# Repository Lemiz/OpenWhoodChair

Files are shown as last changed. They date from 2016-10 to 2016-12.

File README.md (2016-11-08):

# OpenWoodChair

This is a fork of the [OpenWheelChair](http://www.openwheelchair.org/). We dropped the PVC pipes and use palette wood instead so that the wheelchair gets cheaper to build, targeting a wider audience especially in developing countries.

We implemented the BYU wheelchair during the 2016 Abylimpics event in Bordeaux, France, and turned the pipes to wood during the Fabrikarium hackathon organized by MHKit in collaboration with the Airbus group in Octobre 2016 at the Airbus facility in Toulouse, France. Working language: French. 

You may also refer to the French version of Open wheelchair on MHKit website: http://myhumankit.org/tutoriels/fauteuil-roulant/

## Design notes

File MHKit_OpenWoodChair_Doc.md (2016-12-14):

# Présentation du projet

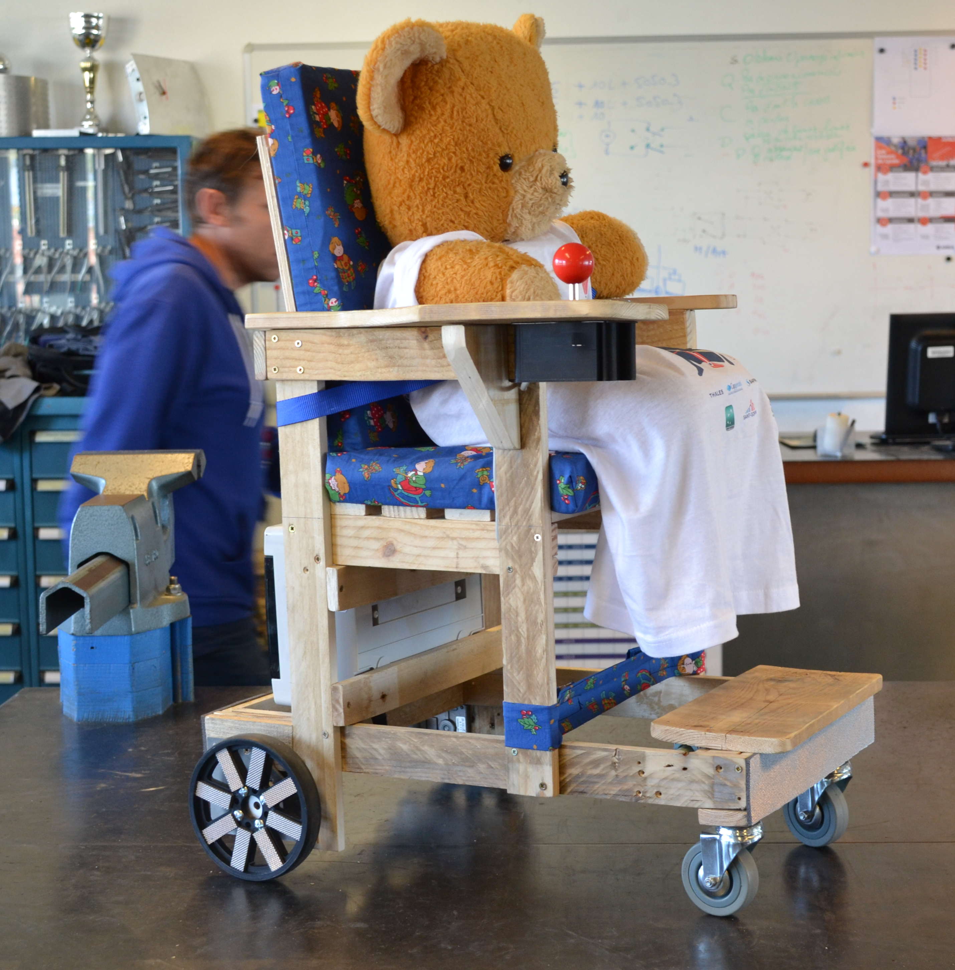
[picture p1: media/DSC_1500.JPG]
Alt Vue du fauteuil assemblé en fin de sprint Fabrikarium Airbus
 *Vue du fauteuil assemblé en fin de sprint Fabrikarium Airbus*
 
OpenWoodChair est une adaptation par l'association My Human Kit du projet Open wheel chair par la fondation américaine du même nom. Le but, que nous partageons avec cet organisme de bienfaisance, est de proposer une liste de pièces, des plans et un manuel de montage pas à pas permettant l'autoconstruction d'un fauteuil roulant en bois motorisé et à faible coût destiné aux enfants. L'idée est de rendre cet équipement réalisable avec un minimum de moyens techniques, en proposant de recycler un maximum de pièces, dont la maintenance et l'évolutivité soient également garanties. Il s'agit d'un processus en constante évolution, qui est documenté ici et publié sous des licences CC-BY permettant son libre usage tout comme sa modification et sa redistribution.

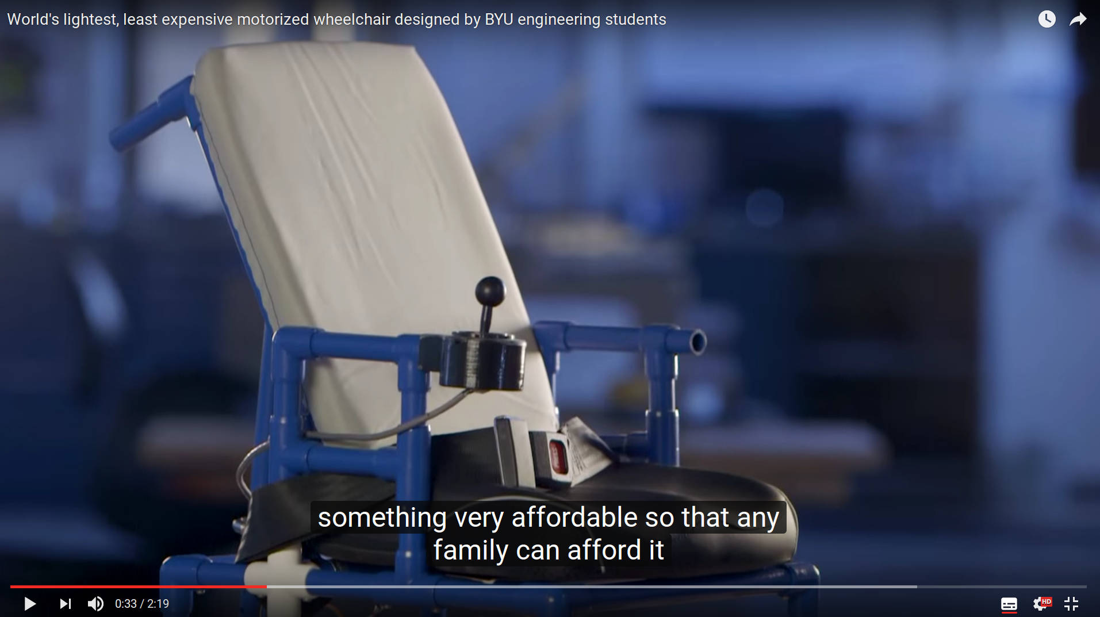
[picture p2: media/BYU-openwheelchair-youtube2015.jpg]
Alt Image extraite de la vidéo de présentation du projet Openwheelchair
. 
*crédits: Brigham Young University News*

La principale innovation du projet OpenWhoodChair réside dans l'abandon des tubes PVC disponible uniquement sur le marché nord-américain de l'ossature au profit d'un matériau recyclé disponible à peu près partout sur la planète, à savoir du bois de palette. On peut également imaginer d'autres adaptations à partir de ressources locales disponibles en abondance à proximité de chez vous, comme le bambou pour l'ossature, du tissu produit localement pour les coussins, etc.
Dans l'idée de rendre le fauteuil compatible avec une propulsion manuelle, nous avons également déplacé les roues motrices de l'avant à l'arrière, de telle sorte qu'il est toujours possible d'assembler le fauteuil sans les moteurs électriques avec de grandes roues classiques.
# Licences
Le matériel est distribuée sous licence CERN Open License Hardware v1.2.  
Sauf mention contraire, toutes photos et illustrations CC 3.0 BY-SA Olivier Heinry.

# Crédits & remerciements

Le projet initial est accessible sur le site de la [fondation Open Wheel Chair](http://www.openwheelchair.org/).

## Sprint Abilympics, Bordeaux, Avril 2016 
Bernadette et Gérard Véron, Jimmy Véron, Yvonne et René Véron, Madeleine et Jean-Louis Delahaye, Jacqueline et Michel You
## Sprint Fabrikarium , Lycée Airbus, Toulouse, Octobre 2016 
Michel & Jacqueline You , Gérard & Bernadette Véron ( afficionados MHK), Patrice Navarri (Airbus Toulouse), Jean-François Soucaille (Airbus Toulouse), Dirk Thalheim (Airbus HH) pour les conseils et retours utilisateur, Marine du Lycée Airbus (pilote d'essai), Olivier Heinry (FLOSS Manuals) pour la documentation, Philippe Pacotte (sympathisant MHK) pour la modélisation et l'impression 3d. 
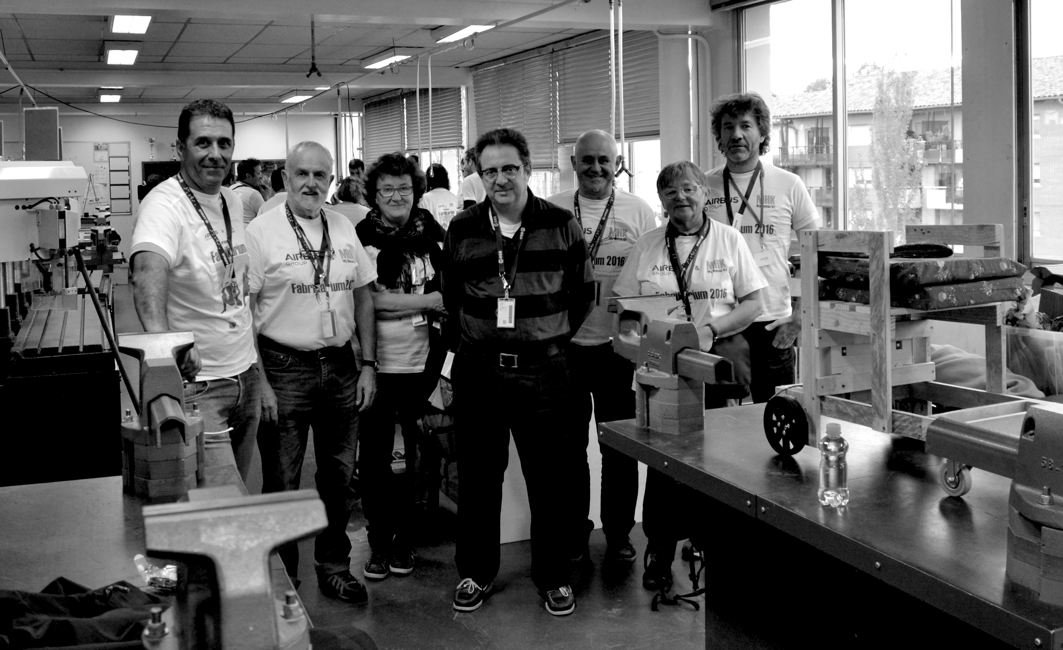
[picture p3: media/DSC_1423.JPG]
Photo de groupe FabrikariumAirbus. Absents: Dirk, Marine & Philippe
 *Photo de groupe lors du Fabrikarium Airbus. Absents: Dirk, Marine & Philippe*

# Avertissement

La liste des pièces et certaines sections de la documentation ne sont pas définitives. Elles seront plus proches de la réalité lors de la prochaine itération au collège Petite Lande de Rezé (44) lors de la semaine du Handicap en 2017. Si d'ici là vous vous lancez dans l'assemblage d'un fauteuil et trouvez des corrections ou voulez soumettre des améliorations, n'hésitez pas à forker le [dépôt Github](https://github.com/MHKit/OpenWhoodChair) et soumettre des pull requests.

# Liste des pièces & fournitures
## Ossature bois
Toutes les pièces de bois de palette suivantes ont une section approximative de 50 x 14 mm.

+ accoudoirs
    
    + montants arrière : 2 x 450mm
    + montants avant : 2 x 530mm2 x 350mm
    + repose-pieds et siège : 7 x 350mm
    
+cadre inférieur

   + 2 x 600mm
   + 4 x 313mm
   + 2 x 83mm
   + 2 x 36mm

+ supports moteur
   + 2 x 83mm
   + 2 x 110mm
+ traverses latérales du siège : 4 x 300mm
+ traverses arrières du siège :
   + 1 x 278mm
   + 1 x 310mm
   + 1 x 345mm
+ repose-pieds: 1 planche de 340 x 140

Métrage total utilisé : 10m. Prévoir de débiter 12m.

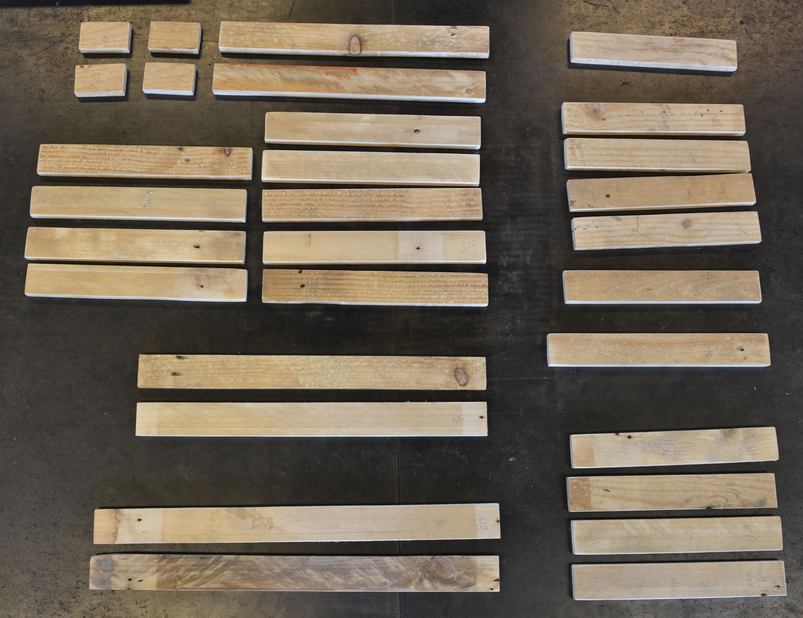
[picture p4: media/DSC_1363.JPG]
Alt Planches débitées. Manquent 2 pièces longueur 110 et 2 pièces de 36mm
 *Planches débitées. Manquent 2 pièces longueur 110 et 2 pièces de 36mm*
+ dossier du siège
   + contreplaqué 9mm : 270x400mm. 

### Astuce
+ Si vous souhaitez rendre les pièces de bois plus durable,vous pouvez les passer à l'huile dure ou bien à l 'huile de lin diluée avec 5-10 % de térébenthine.
+ Pour le contreplaqué, utilisez du bois d'intérieur classé E1, dont les colles dégagent peu de COV toxiques. 

/* màj flossmanuals s'arrête ici */

## Groupe de propulsion
* Plaques de fixation des motoréducteurs  
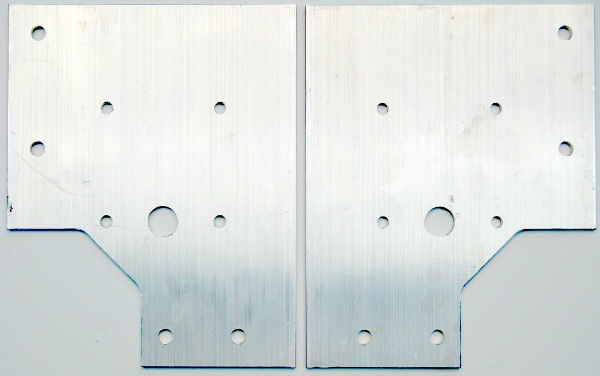
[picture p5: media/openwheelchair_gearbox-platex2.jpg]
plaque de support du motoréducteur
 *plaque de support du motoréducteur*

Ces plaques sont utilisées pour monter les motoréducteurs sur le châssis. Référence GEARBOX-PLATE 14,95$ le lot de 2 chez [www.openwheelchair.org] (http://www.openwheelchair.org/Products/GearBox-Plate/) US$ 14,95 + frais de port
Vous pouvez également les usiner vous-même. Les plans sont en ligne sur https://github.com/OpenWheelchair/Wheelchair-Frame malheureusement dans un format fermé (Solidworks).
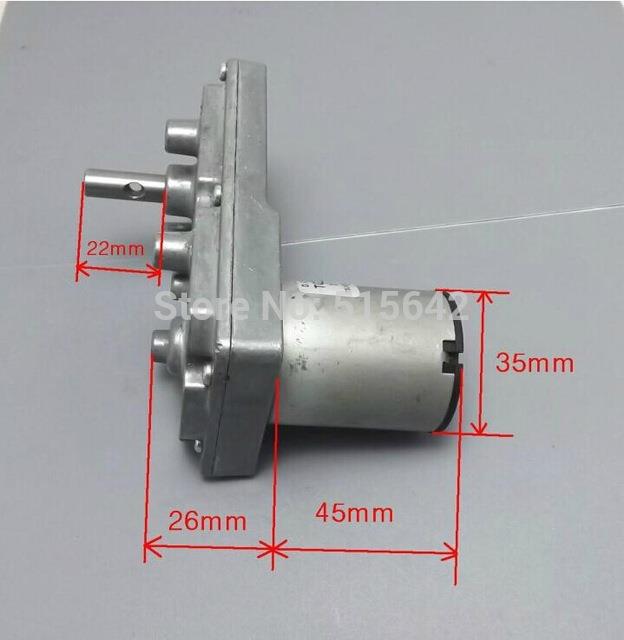
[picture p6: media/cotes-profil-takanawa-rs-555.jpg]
Alt motoréducteurs
* 2 motoréducteurs Takanawa RS-555  *Motoréducteur*

Budget : 10 à 20 US$ sur Ebay ou Aliexpress. 

+ 2 roues folles diamètres 100mm
+ 2 roues pleines diamètre 6 pouces (soit 18 cm) avec un axe diamètre M4 (référence Openwheelchair)

## Coussins & ceinture
### Assise
* mousse d'épaisseur 50mm: 350 x 270 
* tissu : deux pièces de 350 x 390 mm
* 2 bandes velcro aka scratch  à coudre de 5 x 2,5cm

### Dossier
* mousse d'épaisseur 50mm: 390 x 300 
* tissu : deux pièces de 350 x 470 mm
* 2 bandes velcro aka scratch  à coudre de 5 x 2,5cm

### Cale-pieds
* 1 lanière de tissu de 120 x 900mm

### Ceinture de sécurité
* 1 sangle avec une boucle de serrage

### Marquage
Découpe de bandelettes réfléchissante dans des plaques d'isolant métallisé réfléchissant pour porte de garage avec une face adhésive. 

+ Bande arrière 370 x 50 mm
+ Bandelettes de dimensions variables à disposer sur les roues motrices

## Visserie & quincaillerie
### Visserie bois
+ vis de 3 x 25 mm (3,5 x 25mm également possible)
+ x vis de 4 x 35 mm
+ x vis de 4 x 45 mm

#### Astuces
+ Il vaut mieux éviter les vis à tête fendue ou Philips qui sont fragiles ne permettent pas d'exercer beaucoup de force lors du vissage et privilégier les têtes Pozidriv ou Torx.
+ Afin d'accélérer le montage, faites en sorte d'utiliser un seul type et une seule taille d'embout. Par exemple, nous n'avons utilisé que du PZ2 lors du montage de notre prototype.

### Visserie métallique
+ 8 boulons poêliers 5 x 50mm

### Quincaillerie
+ Axe du repose-pieds  
   + un bout de tringle à rideau ou un tuyau de plomberie de 340mm de longueur
   + 2 colliers simples de plomberie dont le diamètre est le double de la tringle ou du tuyau
+ 2 écrous et 2 rondelles du diamètre des roues folles 
+ Un bib de colle à bois vinylique prise rapide

## Electronique & électricité
+ un joystick à contacts fin de course
+ 1 Arduino/Genuino Uno
+ un PCB DFrobot DC Motor Driver 2×15A - Lite ref. SKU:DRI0018
+ un interrupteur
+ du câble électrique souple 0,75mm2
+ 1.5m de câble Ethernet 4 paires
+ une batterie 12V
+ un connecteur à barillet (dit jack)
+ un boitier électrique étanche. Le modèle utilisé ici: Coffret étanche DEBFLEX 12 modules - ref : 706722 : H : 20 cm, L : 27 cm, P : 12 cm. Il doit surtout être assez grand pour loger batterie, circuit de charge, Arduino et driver
+ une vingtaine de câbles Dupont mâle/mâle 20cm  de couleur

## Outillage
Vous aurez besoin des outils suivants pour assembler le fauteuil roulant, disponibles dans n'importe quel magasin d'outillage. Le seul outil spécialisé dont vous aurez besoin (il s'agit de l'extracteur de pignon) est optionnel, et n'est nécessaire que si vous souhaitez passer à des moteurs plus puissants.
### Electroportatif
* une perceuse à colonne OU une perceuse filaire SINON une visseuse sans fil fera l'affaire
* une visseuse sans fil OU un jeu de tournevis
* une ponceuse OU du papier de verre grain 50, grain 120 voire plus fin si vous tenez à avoir une finition d'ébéniste
* une meuleuse avec disque métal peut être utile pour couper les boulons et vis à bois trop longs
* une machine à coudre OU une aiguille et de l'huile de coude

### Outillage manuel
* Jeu de clés 6 pans dites Allen (métrique)
* Jeu d'embouts type Pozi driv ou Torx suivant votre approvisionnement en vis
* Forets à bois diamètre 2,75 (ou 3) et 6
* un fer à souder 30W et un peu de brasure
* un mètre ruban métallique
* une équerre
* un niveau à bulle
* un crayon à bois et/ou une pointe sèche
* des colliers de serrage électrique parfois appelés Rilsan ou Colson
* des cosses électriques plates
* un multimètre
* des serre-joint OU presse à bois OU des pinces-étau
* du frein-filet faible résistance type Loctite 222 OU du vernis à ongle
* un pied de biche, une masse & des tenailles pour le recyclage des palettes
* un masque à poussière, des bouchons d'oreilles, des lunettes de protection, des gants de manutention
* des ciseaux de couturière et un mètre ruban souple
* une règle 50+ cm qui ne marque pas le tissu

### Option: extracteur de pignon 
Utilisé pour retirer le pignon du moteur d'origine pour le remplacer par un moteur plus puissant. Quelques références en ligne:

+ AliExpress  : Puller-Remover-Walkera-W010
+ Hobbyking.com : Product id : S630

# Instructions de débit du bois de palette

## Étape 1: Mesures de votre enfant
Les cotes données dans la liste des pièces correspondent à la stature d'un enfant de 4 ans (taille de 102 cm. Source: http://www.labonnetaille.com/guide-des-tailles/enfant-bebe-mode-vetements). Si votre enfant est particulièrement grand, vous pouvez rallonger de quelques dizaines de millimètres les cotes des accoudoirs et des montants arrière et avant, éventuellement la profondeur du siège. Par contre, le châssis sur lequel sont fixés roues et moteurs ne doit pas voir ses dimensions évoluer.

## Étape 2 - Acheter et rassembler les matériaux et  outils 
Procurez-vous les différents matériaux figurant sur les pages "liste des pièces" et "liste d'outils". Si vous ne trouvez pas certaines pièces, libre à vous d'adapter aux matériaux disponibles à proximité.

## Étape 3 – Démonter les palettes
Il existe beaucoup de qualités différentes de palettes, qui peuvent servir à transporter de tout, entre autres des produits toxiques. Faites donc bien attention dans le choix de votre matière première.  Privlégiez les palettes portant le marquage NIMP 15 ressemblant à un épi de blé et les initiales HT, signifiant qu'elles ont subi un traitement thermique non-toxique contrairement au marquage BM signifiant un traitement au bromure, nocif. Ce dernier est interdit au sein de l'UE depuis 2010.

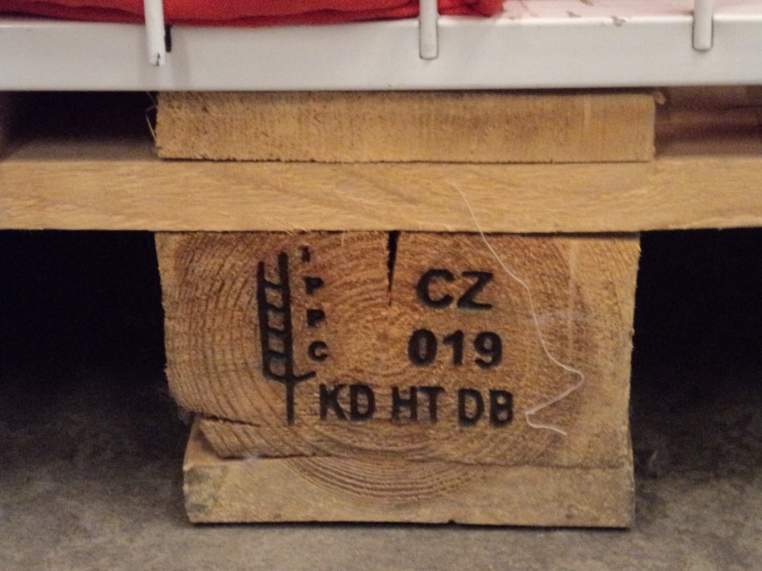
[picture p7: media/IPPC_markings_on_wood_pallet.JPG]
Alt By self-made by the uploader - Own work, CC BY-SA 2.5 ca, https://commons.wikimedia.org/w/index.php?curid=25071284
 
*self-made by the uploader, CC BY-SA 2.5*

Choisissez des palettes fraîchement assemblées, le bois séché exerçant plus de contrainte lors du retrait des clous et agrafes.

#### Astuce
N’oubliez pas de porter vos équipements de protection lors du démontage: lunettes de protection, gants et bouchons d'oreille, chaussures de sécurité et  vaccin contre le tétanos.

Posez la palette à l'envers sur votre plan de travail. Avec le pied de biche, ôtez les clous des semelles: commencez par la planche du milieu, elle est  plus facile à enlever. Réservez les planches.

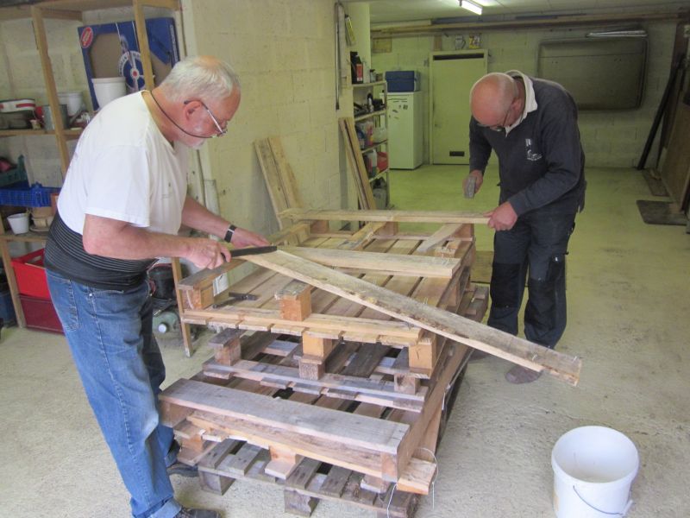
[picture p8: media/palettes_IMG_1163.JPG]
 
*CC 3.0 BY-SA Jacqueline You*

Posez ensuite la palette au sol toujours sur le dos (son plancher) et chassez les chevrons (les blocs quadrangulaires) avec la masse.

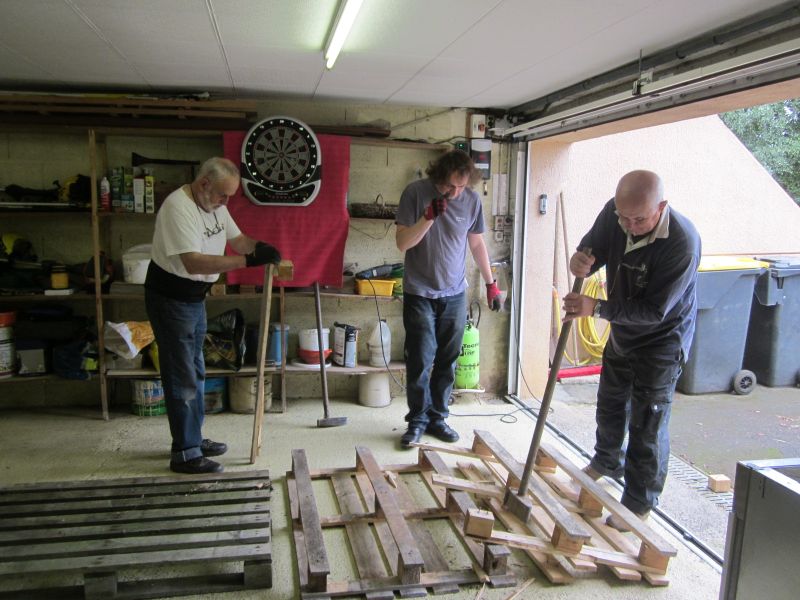
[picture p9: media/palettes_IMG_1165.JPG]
 *CC 3.0 BY-SA Jacqueline You*

Une fois ceci fait, il faut retirer les agrafes et clous restants. On commence par marteler les agrafes du côté des chevrons et on finit de les extraire avec les tenailles.

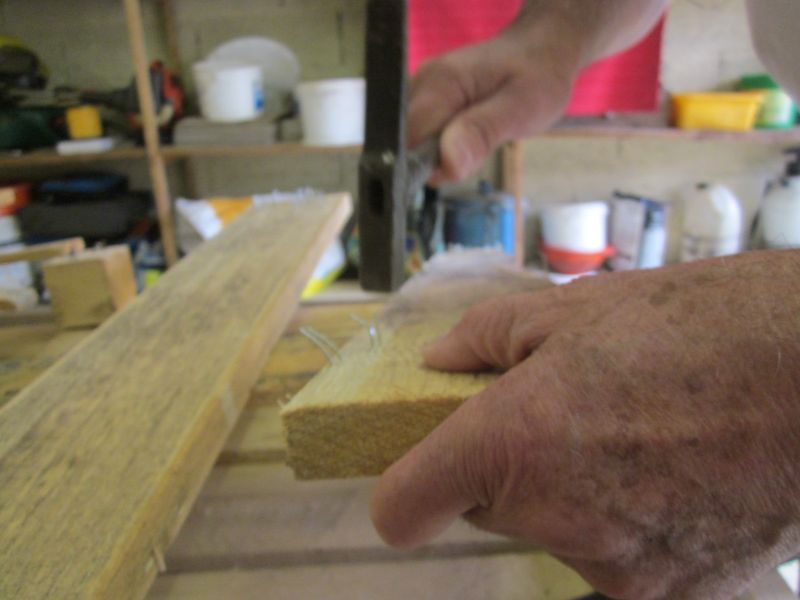
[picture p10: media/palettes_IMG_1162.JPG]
 
*CC 3.0 BY-SA Jacqueline You*

On récolte ça:

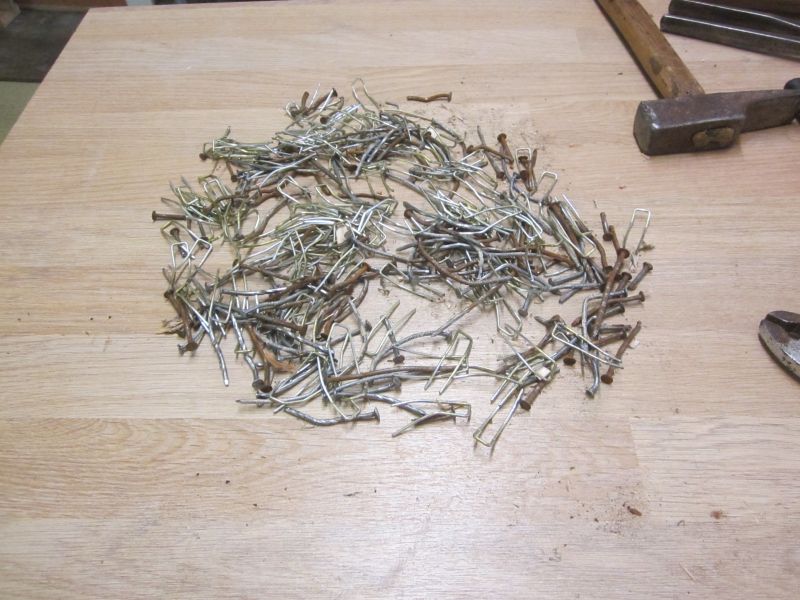
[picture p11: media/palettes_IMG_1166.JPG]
 
*CC 3.0 BY-SA Jacqueline You*

Finalement,on passe au ponçage des planches afin de faire disparaître les échardes , étape au cours de laquelle le port du masque est hautement recommandé. Vous voilà avec un stock de matière première!

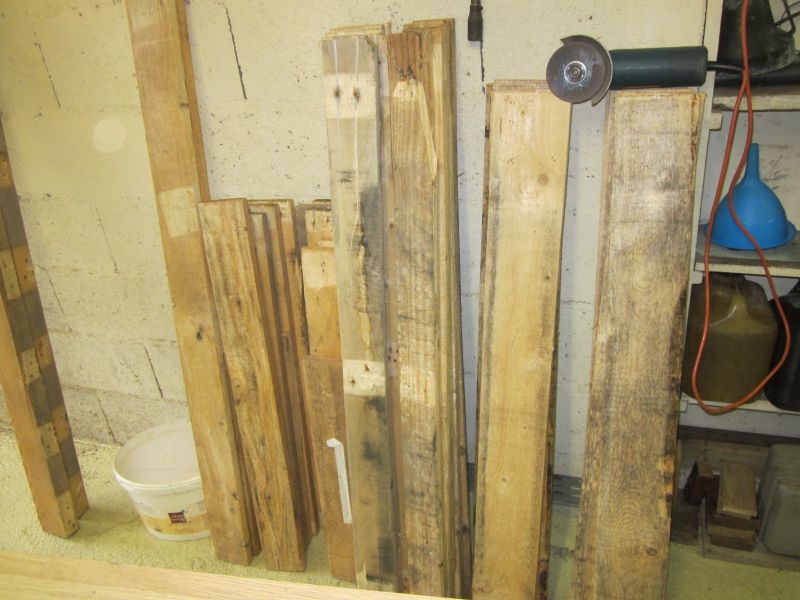
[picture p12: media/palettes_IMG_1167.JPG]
 
*CC 3.0 BY-SA Jacqueline You*

## Etape 4 - Débiter le bois de palettes
On commence par débiter les planches les plus longues, en faisant attention aux nœuds, potentiellement cassants, où aux fentes qui sont apparues au démontage, particulièrement de bois sec. Vous pouvez le faire avec une scie électrique à onglet, à défaut avec une scie à main dans une boîte à onglet. Reportez-vous au paragraphe Ossature bois du chapitre précédent pour consulter la liste des planches nécessaires.

version électroportative *version électroportative*
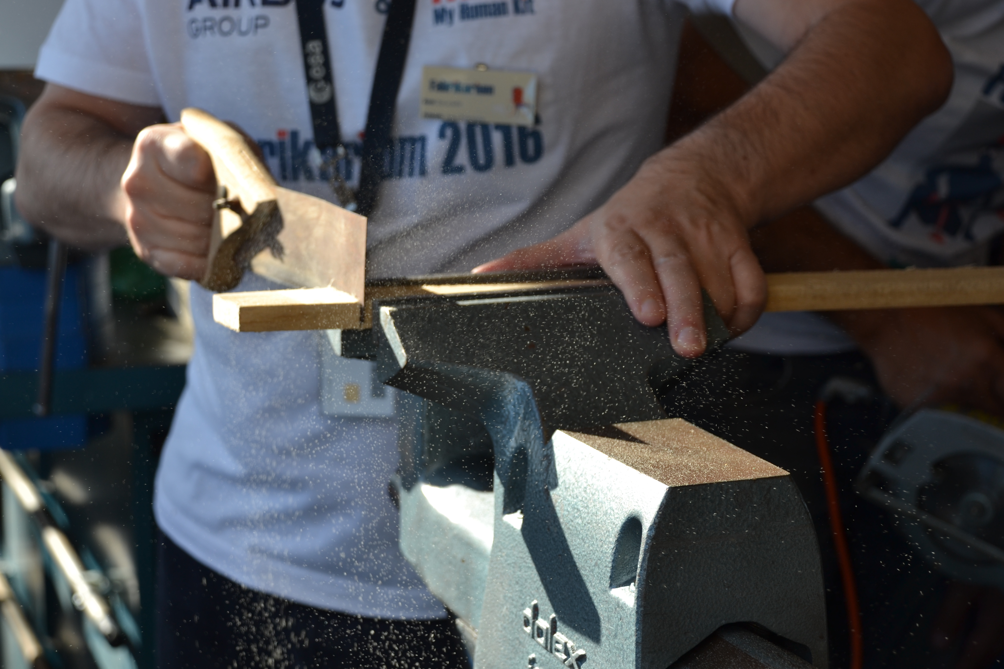
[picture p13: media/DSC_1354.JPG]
Alt version manuelle
 *version manuelle*
Il est également utile de casser les angles vifs après le débit en passant rapidement la ponceuse inclinée à 45°.

# Instructions de montage
Le cadre en bois sera assemblé en 2 parties: tout d'abord la base,  puis les accoudoirs et enfin le siège avec son dossier. Le bloc propulsion, le repose-pieds et les coussins seront assemblés à la toute fin.

## Préparation de gabarits

Afin de garantir la régularité de l'alignement des perçages, nous commençons par construire deux gabarits de perçage. Le premier servira à réaliser les préperçages de bout de planche et le second pour les  préperçages latéraux. 

#### Gabarit de vissage de bout
Prenez une chute, découpez son extrémité proprement à 90°. Tracez ensuite un trait parallèle à l'extrémité à une distance correspondant à la moitié de l'épaisseur du bois de palette. Exemple: si votre bois de palette fait 14mm d'épaisseur, vous tracez un trait à 7mm de l'extrémité pour que la vis pénètre au coeur du bois. Vous percerez ensuite 2 trous à 10 mm de chaque bord avec un foret à bois d'un diamètre en dessous du diamètre de vos vis, afin que le fil puisse encore mordre le bois sans pour autant le faire éclater.

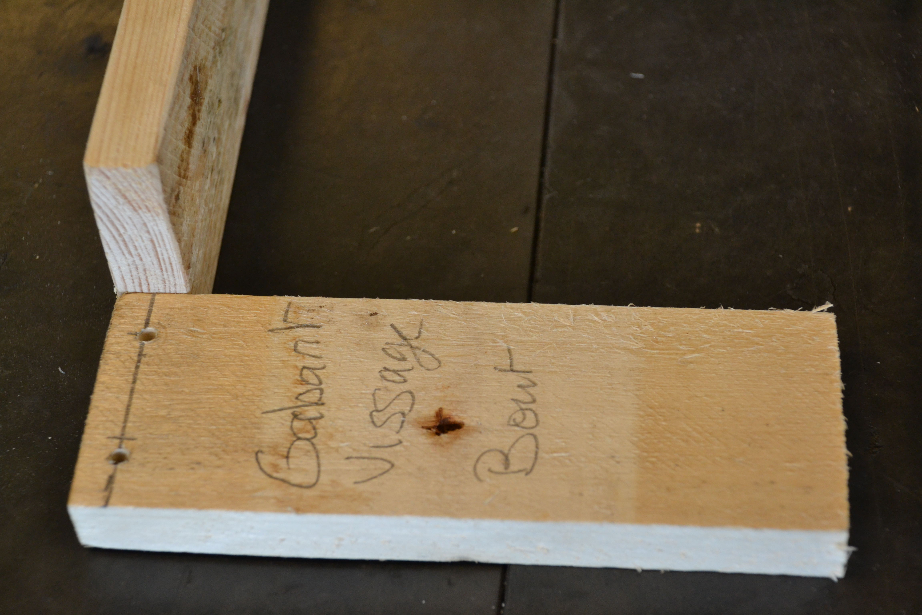
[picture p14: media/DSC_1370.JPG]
Alt gabarit de bout
 

*gabarit de bout*

#### Gabarit de vissage latéral
Prenez une chute, découpez son extrémité proprement à 90°. Tracez ensuite un trait parallèle à l'extrémité à une distance correspondant à la largeur du bois de palette (dans notre cas, 50mm). Tracez ensuite les diagonales. Vous percerez ensuite 4 trous à 15 mm de chaque angle avec le même foret que précédemment.
Alt gabarit latéral 

*gabarit latéral*

#### Astuce
L’assemblage va beaucoup plus vite si vous organisez vos planches en paquets suivant les dimensions. Vous pouvez noter la cote directement sur la pièce comme nous l'avons fait ici au porte-mine, note qui sera enlevée par ponçage une fois l'assemblage fait.

## Assemblage de la base du châssis
### Assemblage du cadre
Rassemblez les différentes pièces nécessaires à cette étape:
+ vis 3x25mm
+ vis 4x35mm
+ 2 x 600mm
+ 4 x 313mm
+ 2 x 83mm
+ 2 x 36mm

On commence par prépercer les planches de 600mm en utilisant le gabarit de vissage de bout. On se contente de marquer sans traverser la planche.
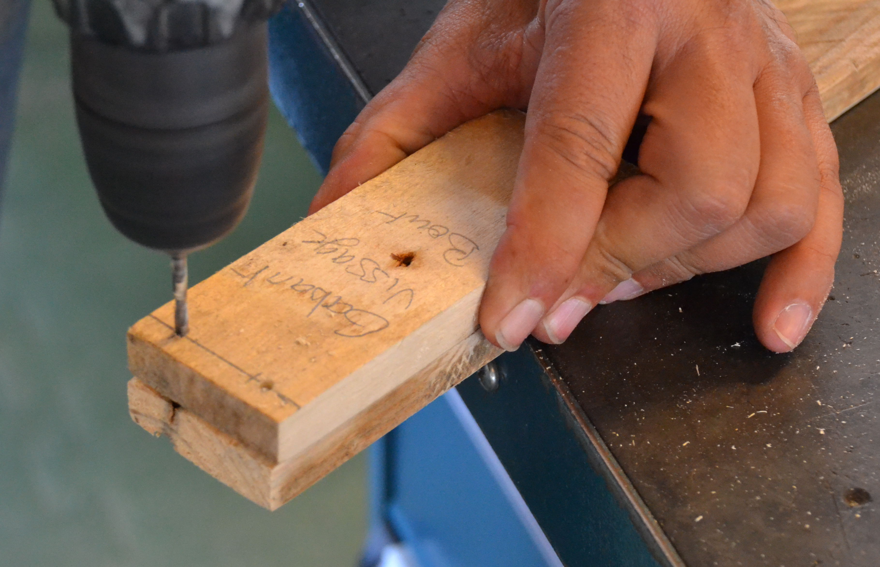
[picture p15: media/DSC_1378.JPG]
Alt préperçage à l'aide du gabarit
 *préperçage à l'aide du gabarit*

On passe ensuite au perçage proprement dit. Cela permet de vérifier que le bois ne fend pas, ou que le perçage n'a pas lieu à un endroit critique comme un noeud ou l'ancien emplacement d'un clou.
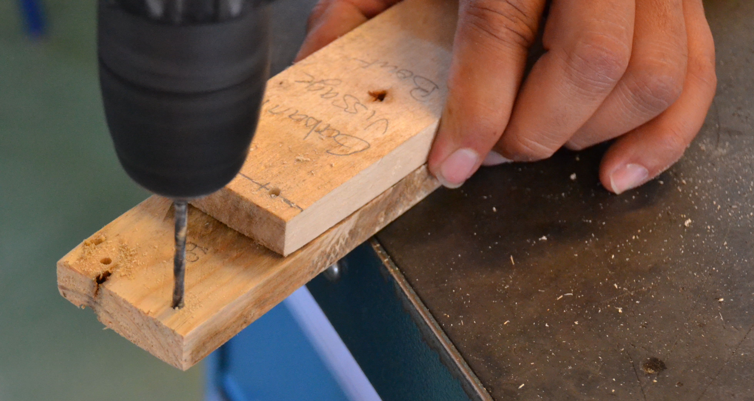
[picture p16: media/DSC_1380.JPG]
Alt Perçage proprement dit
 *Perçage proprement dit*

Disposez ensuite les  2 planches de 313 mm à l'intérieur des planches de 600mm, en vérifiant le bon équerrage. On visse en 4x35mm. Vosu devez obtenir un cadre rectangulaire, pas un trapèze. 
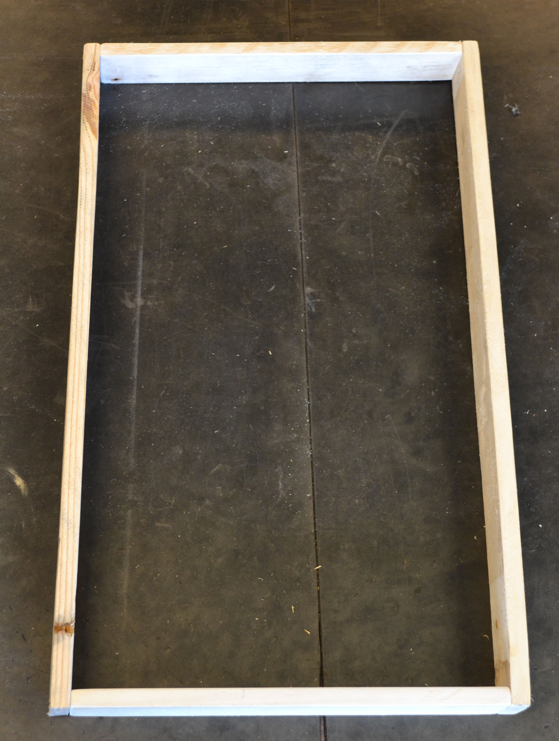
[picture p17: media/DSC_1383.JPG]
Alt Cadre assemblé
 *Cadre assemblé*

### Ajout de renforts
Nous devons maintenant assembler 2 planches de 83mm à l'intérieur des planches de 600mm, au niveau de ce qui portera les futures roues motrices. On commence par marquer l'épaisseur de la planche, puis on utilise la gabarit de vissage latéral aligné sur cette marquer pour prépercer la première vis.
Alt Préperçage du renfort *Préperçage du renfort*

On visse avec deux vis 3x25; attention de ne pas noyer la tête pour seulement affleurer du côté intérieur.
Alt Vissage du renfort *Vissage du renfort*

On peut ensuite assembler la traverse de 313mm avec quatre vis 4x35 pour obtenir un montage dont on vérifiera l'équerrage avant de visser définitivement.
Alt Assemblage des renforts et de la traverse *Assemblage des renforts et de la traverse*

On répète l'opération à l'autre extrémité. Attention: il faut utiliser les entretoises de 36mm à l'avant, contrairement à ce qu'indique la photo! En effet, nous avons ajouté par la suite un repose-pieds basculant qui a nécessité de déplacer vers l'avant la traverse. 
Alt Assemblage final du cadre *Assemblage final du cadre*

## Assemblage des accoudoirs

Rassemblez les différentes pièces nécessaires à cette étape:
+ montants arrière : 2 x 450mm
+ montants avant : 2 x 530mm
+ traverses latérales du siège : 4 x 300mm
+ 12 vis 3x25mm
+ de la colle à bois

Disposez face à vous en les alignant les extrémités des 4 montants. Utilisez le gabarit de vissage latéral pour marquer 2 préperçages à chaque extrémité. Marquez ensuite chaque montant d'un trait à 245mm de l'extrémité prépercée. Répétez l'opération de préperçage.
Alt Nous avions ici déjà assemblé la traverse du haut. Il est plus aisé de commencer par le marquage simultané de tous les montants avant assemblage. *Nous avions ici déjà assemblé la traverse du haut. Il est plus aisé de commencer par le marquage simultané de tous les montants avant assemblage*

Assemblez ensuite 2 traverses de 300mm avec un montant de 450mm et un montant de 530mm. 
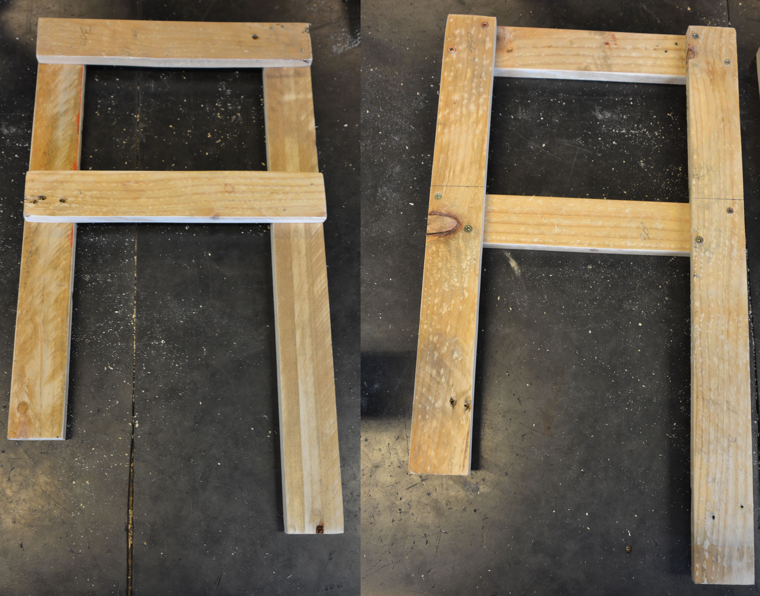
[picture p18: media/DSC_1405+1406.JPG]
Alt Vue recto-verso du premier accoudoir
 *Vue recto-verso du premier accoudoir *

Répétez l'opération pour l'accoudoir suivant, avec les 4 montants du côté opposé. Lors de l'assemblage final, les traverses du bas supporteront l'assise et celles du haut la tablette horizontal de l'accoudoir.

Marquez ensuite le montant de 530mm à 80mm de l'extrémité laissée libre et utilisez le gabarit de vissage latéral pour y faire 2 prépercages. Prépercez également le montant de 450mm.
Alt Le bon usage de l'autofocus facilite la lecture du mètre-ruban :) *Le bon usage de l'autofocus facilite la lecture du mètre-ruban :)*

Vous pouvez alors assembler le premier accoudoir en l'alignant à la verticale du trait à 80mm à la base du chassis et l'extrémité du montant le plus court. L'arrière de montant le plus long doit se caler à l'extrémité de la traverse du chassis.
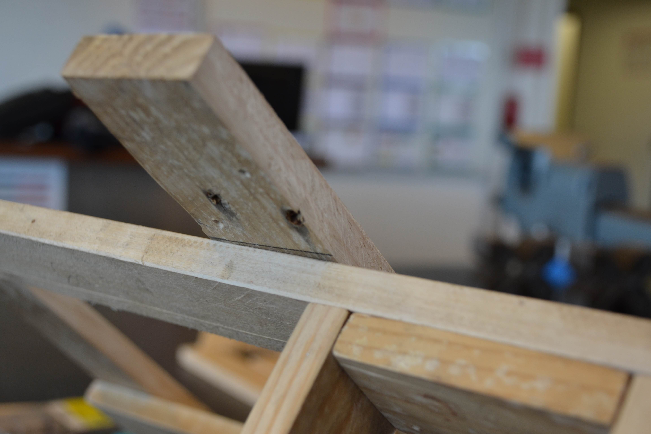
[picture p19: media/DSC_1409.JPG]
Alt Vue d'ensemble
 *Vue d'ensemble*

On doit ajouter de nouveaux renforts qui doivent mieux répartir les fortes contraintes liées à l'assemblage des roues motrices à cet endroit. Ces pièces doivent courir de l'extrémité du cadre jusqu'aux montants arrière des accoudoirs. Il vaut mieux les mesurer plutôt que de les couper au préalable. Dans notre cas, elles font 112mm au lieu des 110mm prévus. Ce n'est pas bien méchant, mais tant qu'on y est...
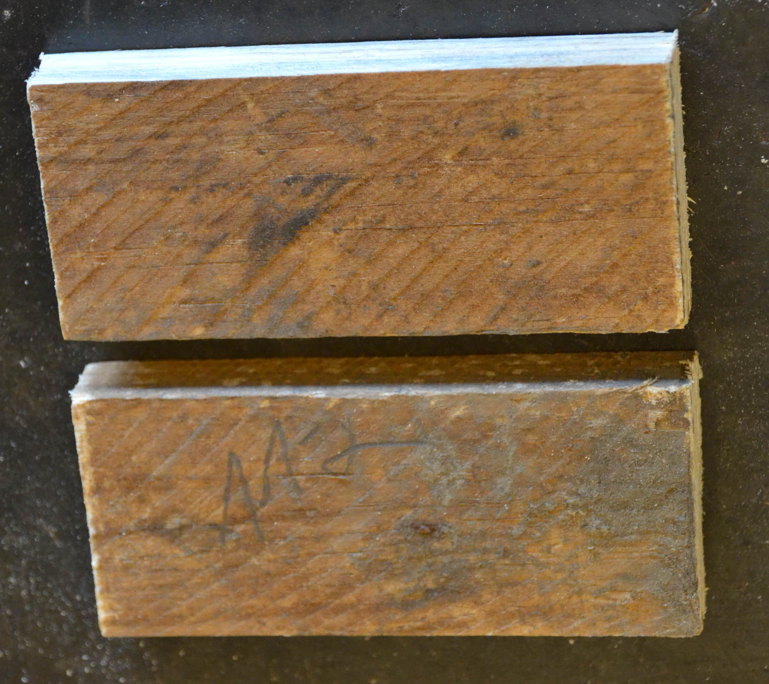
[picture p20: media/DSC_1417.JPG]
alt Cales de 110mm qui font 112mm dans la vraie vie
 *Cales de 110mm qui font 112mm dans la vraie vie*

On est libre d'utiliser le gabarit de vissage latéral ou pas. Un peu de colle à cet endroit ne peut pas faire de mal non plus.
Alt Cales assemblées *Cales assemblées*

## Montage des roulettes
Rassemblez les différentes pièces nécessaires à cette étape:
+ traverse: 1 x 345mm
+ 2 roues folles diam. 100mm
+ 6 vis 4x35mm
+ de la colle à bois

On commence par visser la traverse horizontale de 345mm sur laquelle seront fixées les roues folles en travers de l'avant du chassis. On utilisera le gabarit de vissage de bout, en travers tout d'abord pour les deux premières vis, puis à 90° sur la traverse avant, où une seule vis suffira. 
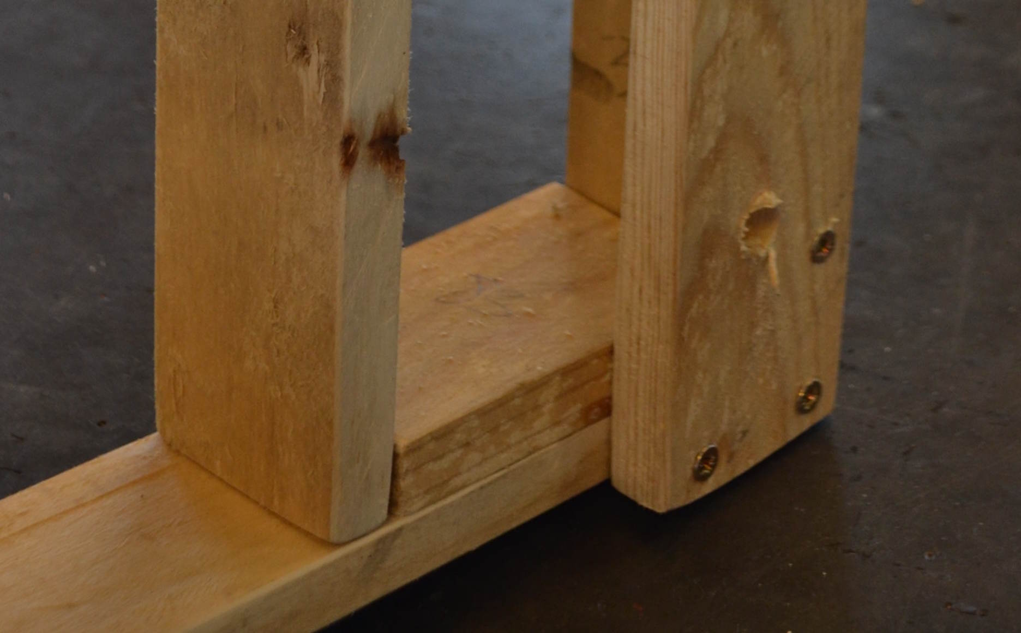
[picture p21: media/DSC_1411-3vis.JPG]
Alt Détail de l'assemblage avec les entretoises de 83mm.
 *Détail de l'assemblage avec les entretoises de 83mm*

On perce ensuite la traverse que nous venons de poser pour laisser passer les axes des roues folles. Le dimaètre de perçage dépend du diamètre de ces axes. Dans notre cas, il s'agissait de M6. On perce alors directement en 8mm sans chercher à utiliser un diamètre inférieur contrairement aux vissages effectuées précedemment, car on boulonne. La position latérale du perçage doit être déterminé en fonction de la largeur totale du fauteuil roulant une fois les roues arrières montées. Il faut ques les roulettes avants puissent pivoter librement à l'intérieur de la largeur totale. Quant à la position en profondeur du perçage, elle a été déterminée de telle sorte que la rondelle et l'écrou puissent être assemblés sur l'axe de la roue folle sans encombre.
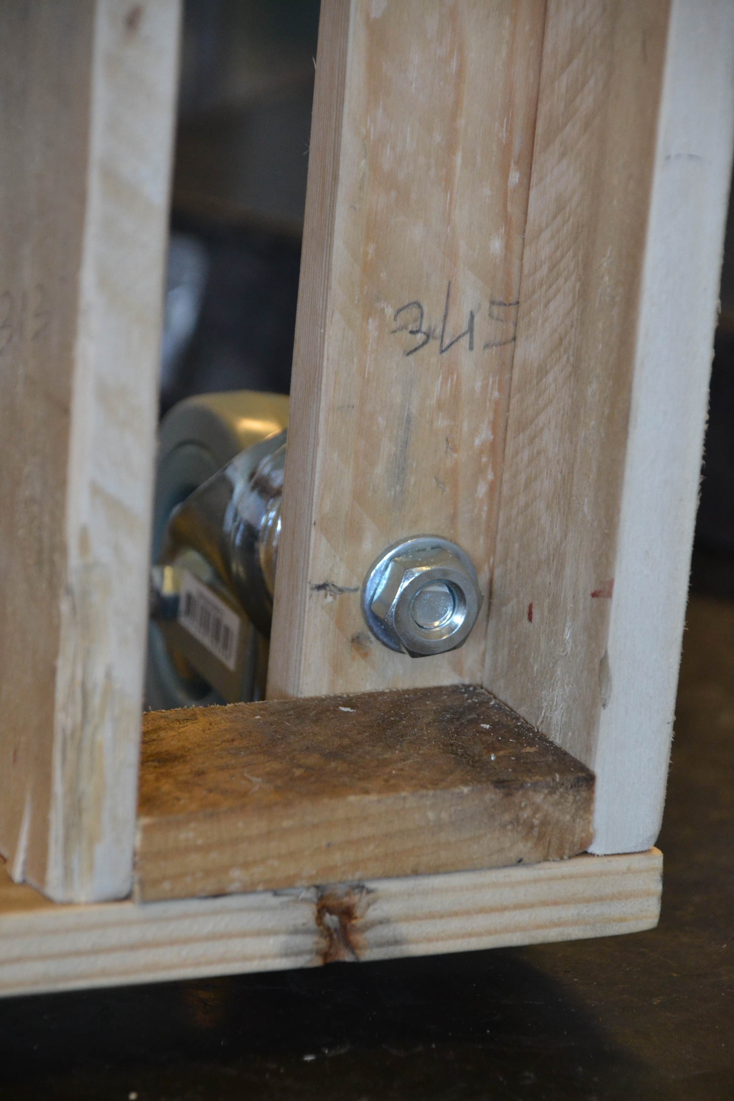
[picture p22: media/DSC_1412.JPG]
Alt Détail du boulonnage avec les entretoises de 83mm.
 *Détail du boulonnage avec les entretoises de 83mm*

Votre assemblage final doit plutôt ressembler à cette illustration. Comme nous devons régler finement plus tard la hauteur, ne serrez pas trop fort.
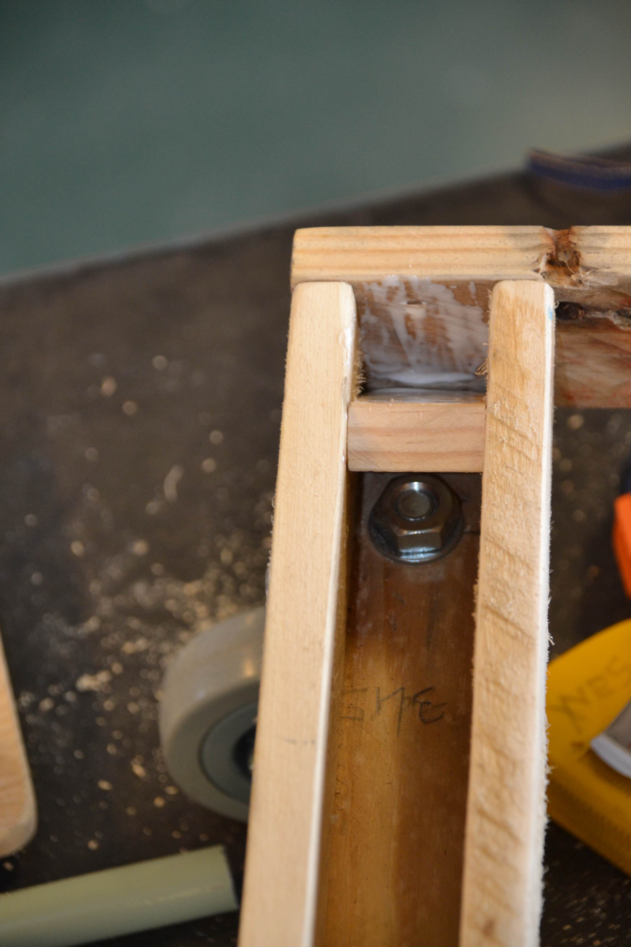
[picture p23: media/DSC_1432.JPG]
Alt Détail du collage a posteriori d'une entretoise de 36mm.
 *Détail du collage a posteriori d'une entretoise de 36mm*

## montage des roues motrices

Rassemblez les différentes pièces nécessaires à cette étape:
+ 2 plaques de fixation des motoréducteurs
+ 2 motoréducteurs Takanawa RS-555
+ 2 roues pleines diamètre 150mm et leurs moyeux
+ 8 boulons poêliers 5 x 50mm + écrous
+ 8 vis m4 x 30mm tête fraisée
+ 4 vis à bois 4 x 45mm
+ 4 vis à bois 2 x 25 mm
+ clé Allen

Nous commençons par assembler la plaque au motoréducteur, puis la roue à l'ensemble. Une fois fait, on soude les câbles d'alimentation électrique. Une fois les 2 roues assemblées, on les fixe au chassis de bois.

### assemblage de la plaque au motoréducteur.
Si vous utilisez des vis à tête fraisé, il vous faudra au préalable fraiser les 8 perçages de petit diamètre, par exemple avec un foret HSS 6mm. Si vous utilisez des vis à tête plates, vous pouvez y aller.
Perçages à utiliser  *Perçages à utiliser cerclés*

Présentez les plaques face au moteur en faisant coïncider les perçages M4 cerclés sur l'illustration . Vissez en utilsant 4 vis m4 après avoir déposé une goutte de freinfilet à mi-filetage. Répétez l'opération avec l'autre ensemble, en faisant attention à l'orientation. Les 2 assemblages sont symétriques et non pas identiques.

### assemblage de la roue 
Assemblez la roue sur son moyeu en répartissant également les quatre boulons poêliers. N'hésitez pas encore une fois à mettre une goutte de freinfilet.
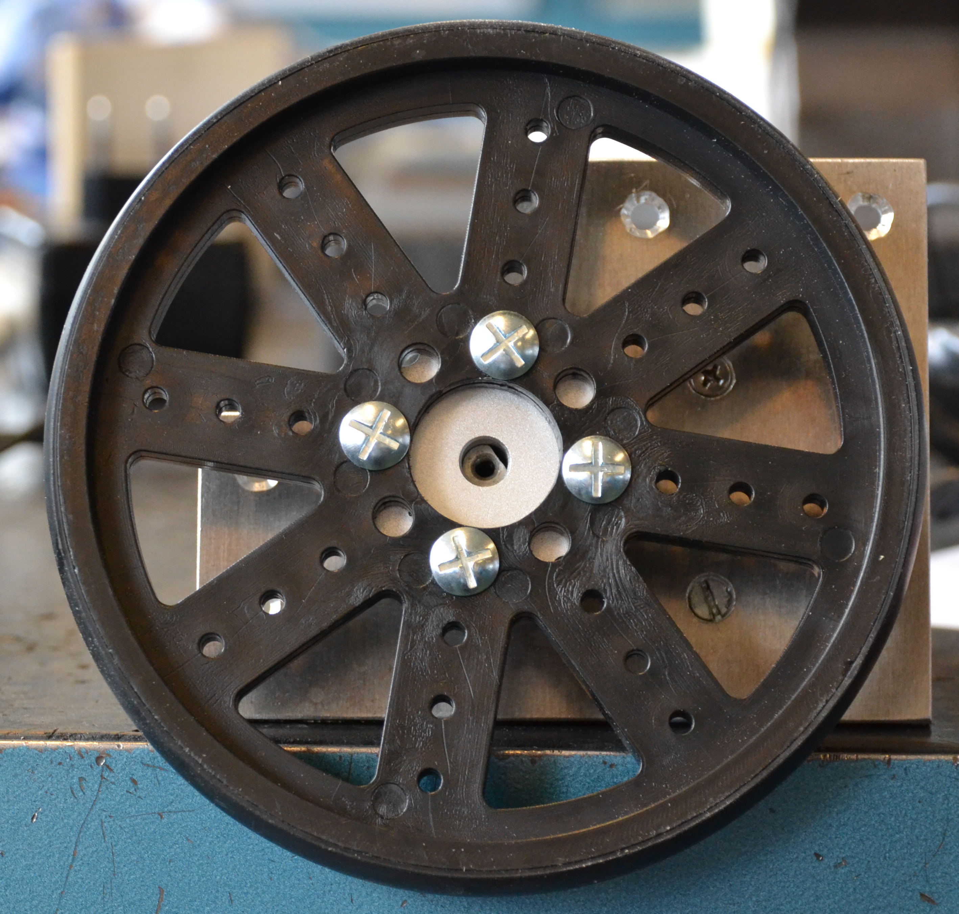
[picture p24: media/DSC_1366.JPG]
Alt Vue latérale de l'assemblage.
 *Evitez d'utiliser des vis cruciformes et fendues comme nous l'avons fait ;-)*
Présentez la roue sur l'axe du moteur. La vis de serrage doit être présentée face au méplat de l'axe. On utilise une clé Allen pour ce faire. Alt vue masse de l'assemblage *Vous pouvez raccourcir les boulons à la meuleuse si vous jugez qu'ils risquent de frotter contre la plaque.*

### montage de l'ensemble
C'est ici une étape cruciale pour le futur comportement roulant du fauteuil. Pour que le fauteuil file droit lorsqu'il court sur son erre, les roues motrices sont disposées à l'arrière. Pour éviter que les roues folles ne se bloquent, leur axe vertical doit être parfaitement vertical. A vous de jouer entre le réglage des boulonnages à l'avant et la hauteur à laquelle vous vissez les blocs moteurs à l'arrière. Pour ce faire, il vaut mieux travailler sur un établi parfaitement horizontal, il suffit de le vérifier à l'aide d'un niveau à bulle. Vous posez ensuite le fauteuil sur cales à l'arrière et sur ses roues folles à l'avant et trouvez la bonne hauteur en vous aidant du niveau à bulle posé parrallèlement à l'axe d'une des roues folles. Vérifiez ceci des deux côtés, sinon le  fauteuil aura tendance à virer.
Ceci fait, vous pouvez présenter votre bloc moteur-roue sur le chassis en présentant la découpe de la plaque par l'avant. Faites un marquage, puis fixez la plaque  en utilisant les vis 4 x 45 mm sur la partie arrière renforcée et les vis 3 x 25mm sur le montant arrière du siège. Vous pouvez passez le tournevis au travers des rayons de la roue.

Alt Vue latérale du montage 
*Vue latérale du montage*

## Fabrication des accoudoirs et boîtier du joystick

Les accoudoirs sont différents mais interchangeables: il suffit de les retourner lorsque vous les changez de côté. L'un des accoudoirs est spécifique en ce qu'il a une forme de palette (de peintre) destinée à abriter le joystick. Vous trouverez le plan au format SVG sur notre dépôt Github dans le dossier  src (https://github.com/oli44/OpenWhoodChair-1/blob/master/media/accoudoir.svg) ainsi que celui de l'équerre de l'accoudoir (https://github.com/oli44/OpenWhoodChair-1/blob/master/media/equerreAccoudoir.svg). Le perçage central mesure 6mm de diamètre, les préperçages de vis à bois sont variables, au minimum le diamètre de votre boulon/vis - 0,5mm de diamètre afin qu'il y ait un peu de friction au serrage.

Alt Plan coté de l'accoudoir 
*Plan coté de l'accoudoir*

Alt Plan coté de l'équerre de l'accoudoir 
*Plan coté de l'équerre de l'accoudoir*

## câblage et impression 3d du boitier du joystick
Afin d'abriter les contacts électriques du joystick de l'arrachement accidentel ou des projections d'eau, il est recommandé de l'abriter dans un boitier isolant. Nous avons modélisé et imprimé un boitier en ABS sur mesure. Vous trouverez les fichiers source sur notre [dépôt Github](https://github.com/MHKit/OpenWhoodChair-1/tree/master/3d).

Avant de placer le joystick dans son boitier, il faut câbler ses contacts de fin de course. Pour cela, il faut dénuder un câble Ethernet 4 paires sur une bonne dizaine de centimètres. Vous dénudez ensuite l'extrémité chacun des 8 câbles colorés sur 1cm, câbles que vous étamez: cela consiste à déposer un tout petit peu de brasure qui doit se répandre par capillarité entre les brins de cuivre. 

Il faut ensuite souder les câbles sur le joystick en suivant le schéma suivant:

Alt Schéma de câblage du joystick 
*Schéma de câblage du joystick*

Toutes les mesures n'étaient pas bonnes, nous avons forcé le passage du joystick dans le logement puis resoudé le plastique avec un décapeur thermique réglé au minimum. Le bâton du joystick a été dévissé afin de pouvoir passer dans le perçage central. L'assemblage du tout a été réalisé le fauteuil posé à l'envers sur l'établi. Nous avons utilisé des boulons poeliers 5x50mm que nous avions en stock après les avoir raccourci à l'aide d'une scie à métaux à une longeur d'environ 25mm, à adapter suivant l'épaisseur de votre bois de palette. On peut très bien utiliser des vis à métaux à tête bombée au lieu de boulon, ou des vis BTR, peu importe les moyens pourvu que ça serre.

Alt Montage final du joystick 
*Montage final du joystick*

Une fois ceci fait, on perce la pièce de bois horizontal sur laquelle repose l'accoudoir, puis la traverse horizontale à l'arrière de l'assise avec un foret permettant le passage aisé du câble 4 paires, dans notre cas, du 6mm.

Alt Perçages du passage de câble du joystick 
*Perçages du passage de câble du joystick*

Il faut ensuite fixer le câble pour qu'il ne pende pas dans le vide. Nous avons utilisé une agrafeuse avec des agrafes de 10mm de large. Il faut être précuationneux et ne pas endommager le câble.

Alt Agrafage du passage de câble du joystick 
*Agrafage du passage de câble du joystick*

Une fois ceci fait, on roule et réserve le reste du câble 4 paires.

## assemblage du boîtier électrique

Nous allons devoir assembler et faire tenir dans un boitier étanche la carte contrôleur Arduino, les pilotes des moteurs, la batterie, l'interrupteur et le connecteur de recharge de la batterie.

Alt Schéma de principe 
*Schéma de principe du montage électrique*

Rassemblez les différentes pièces nécessaires à cette étape:
+ le boitier électrique étanche
+ le connecteur à barillet de recharge de la batterie
+ la batterie 12V
+ l'interrupteur
+ la carte driver de moteur DC de DFrobot
+ la carte Arduino Uno
+ du câble souple 0.75mm2 de préférence rouge et noir
+ 14 câbles Dupont mâle/mâle de couleur
+ de la gaine thermorétractable

Il y a peu de chance que vous retrouviez exactement les mêmes composants que nous lors de ce montage, surtout si vous utilisez des pièces de récupération. Il vaut donc mieux entreprendre de monter à blanc une première fois avant de réaliser les perçages en adaptant les diamètres et les emplacements à votre matériel.

### câblage du joystick vers le microcontrôleur Arduino

Vous allez devoir relier via un câble dupont sectionné en 2 chacun des câbles provenant du joystick en réalisant une simple épissure et en ajoutant un point de brasure. Une fois fait, on enfile un peu de gaine thermorétractable et on donne un coup de fer pour assembler le tout.

Alt Câblage du joystick vers l'Arduino 
*Câblage du joystick vers l'Arduino. Les gaines thermo noires ont été posées trop tôt. Faites ce que je dis, pas ce que je fais!*

Voici le tableau de correspondance depuis le câble 4 paires vers les Dupont:

+ orange vers orange
+ marron/blanc vers jaune
+ bleu vers bleu
+ vert vers vert
+ vert/blanc vers gris
+ bleu/blanc vers noir
+ rouge vers violet
+ orange/blanc vers blanc

On raccorde ensuite les 4 pins positifs des fins de course du joystick comme suit:

+ bleu vers digital 8
+ orange vers digital 9
+ vert vers digital 10
+ jaune vers digital 11

Les 4 autres câbles Dupont, respectivement gris, noir, violet et blanc doivent être raccordés à la masse de l'Arduino, marquée GND sur la carte en 2 emplacements respectivement du côté des ports analogiques et des ports digitaux. Pour ce faire, nous avons utilisé un petit bout de plaque de prototypage reliant ces 4 câbles via un connecteur monté sur la plaque reliés au verso par un dépôt de brasure, puis vers le pin GND de l'Arduino mais vous pouvez procéder de toute autre manière.

### câblage des moteurs vers la carte driver

Il est primordial de câbler les moteurs de façon identique. Si vous ne le faites pas, les moteurs tourneront dans des sens opposés, et le fauteuil tournera sur lui-même alors qu'on souhaite filer droit. Des pinces crocodiles sont pareticulièrement pratiques à cette étape. Pour ce faire, marquez chacun des connecteurs d'un moteur soit d'un point noir soit d'un point rouge. Branchez le pôle négatif de la batterie sur le 0 avec un câble noir, puis le pôle positif sur le 1 avec un câble rouge. Observez dans quel sens la roue tourne. Effectuez le branchement sur le moteur de la seconde roue sans avoir marqué les polarités. Si elle ne tourne pas dans le même sens que la première, intervertissez le câblage, vérifiez que les deux roues tournent dans le même sens et notez les bonnes polarités d'un point coloré au feutre.

Alt Câblage du driver vers l'Arduino 
*Câblage du driver vers l'Arduino.*

Dans notre cas, nous avons procédé de la manière suivante:

broches arduino	| broches PCB
-------------|------------
D4 | M2_EN
D5 | 		M1_pwm
D6 | 		M2_pwm
D7 | 		M1_EN
5V |	5V	
GND |		GND

Vous trouverez des informations détaillées concernant cette carte sur le [wiki du fabricant](https://www.dfrobot.com/wiki/index.php/DC_Motor_Driver_2x15A_Lite_(SKU:_DRI0018))

### câblage de l'interrupteur et de la batterie

### câblage de la carte driver vers le microcontrôleur Arduino

### tests

# Confection

## Coussins

Alt coussins 
*Patrons des coussins.*

## Lanières du cale-pieds

Alt Patrons des lanières du cale-pieds. 
*Patrons des lanières du cale-pieds.*

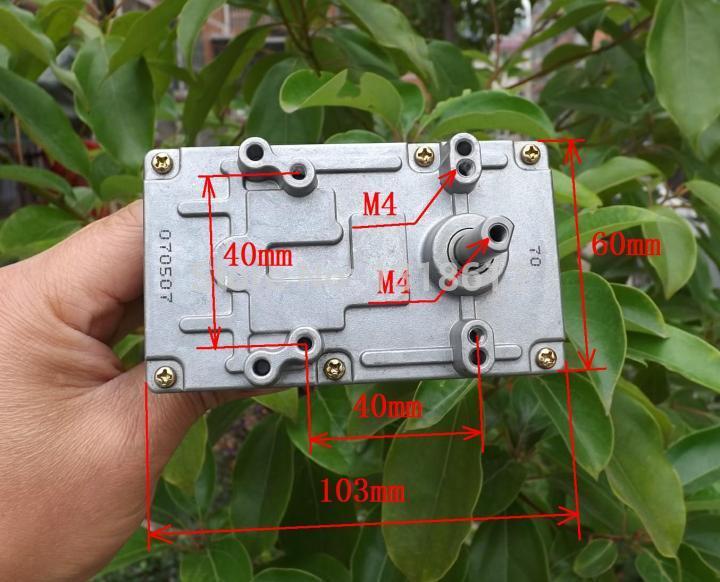
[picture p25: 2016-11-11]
media/takanawa-rs-555-cotes-fixations.jpg

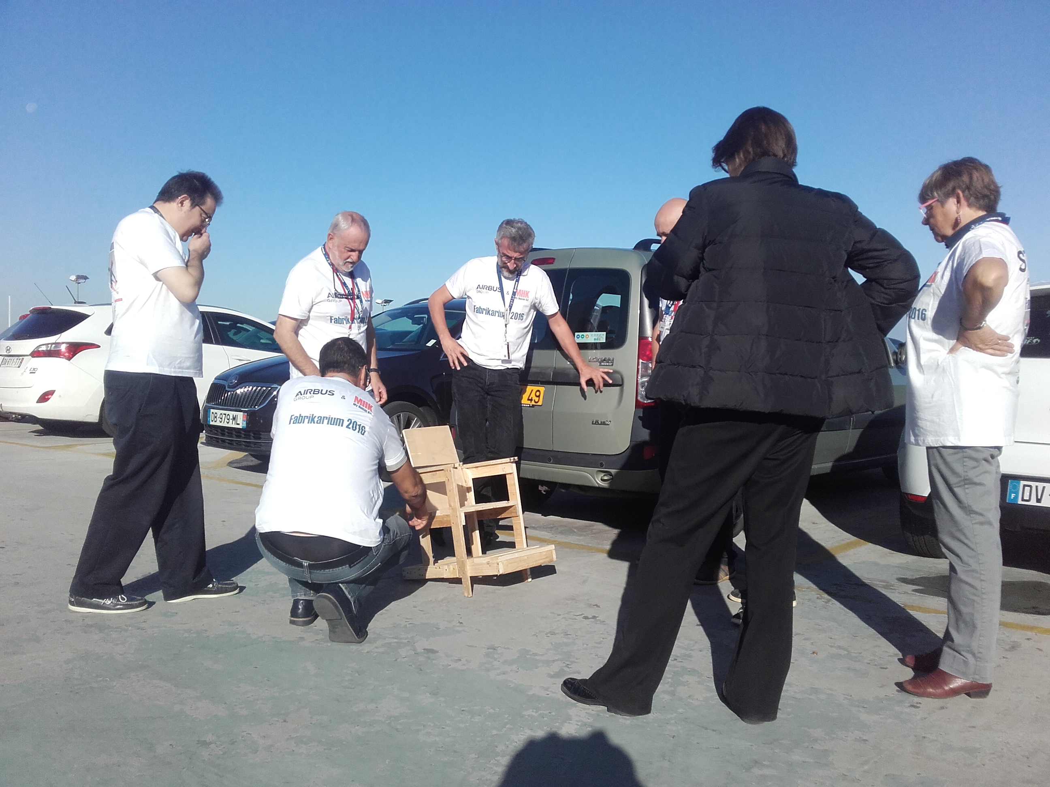
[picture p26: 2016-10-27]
media/auculducamion20161019_103545.jpg

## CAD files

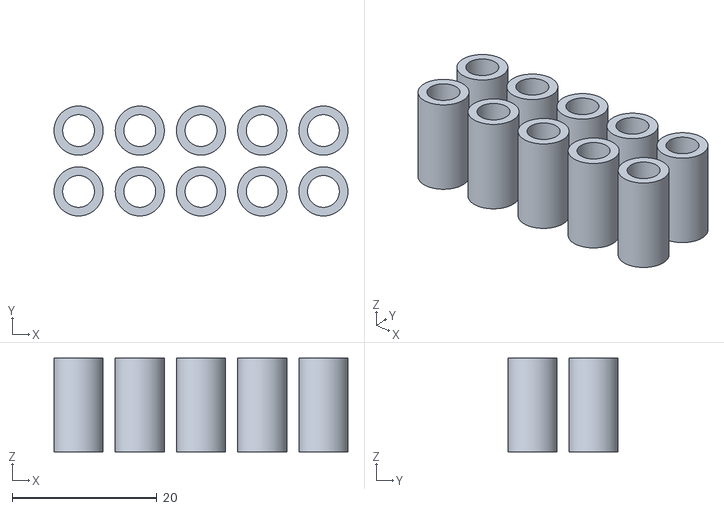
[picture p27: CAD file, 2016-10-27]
3d/entretoises.stl
40.7 x 15.2 x 13.0

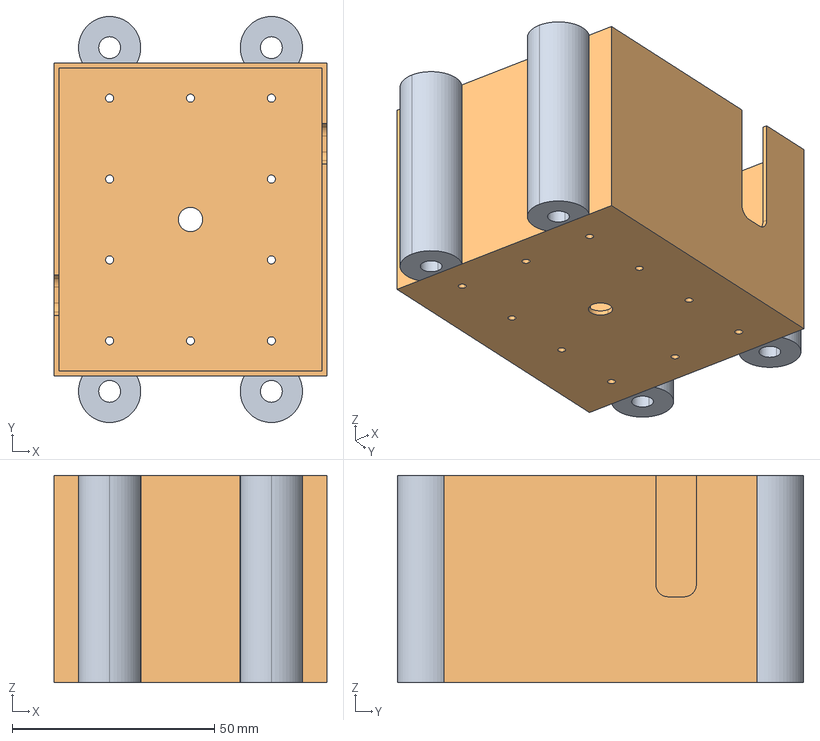
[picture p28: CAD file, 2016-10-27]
3d/boitier joistick.stp
67.4 x 100.4 x 51.2 mm

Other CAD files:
3d/boitier joistick.igs
3d/boitier joistick.obj
3d/boitier joistick.stl

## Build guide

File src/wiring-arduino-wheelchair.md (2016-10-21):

//@hugobiwan

Wiring open wheelchair / arduino

Prototype actuel : deux nappes sortent du joystick.

--------------JOYSTICK------------------------

> Une nappe GND (VIOLET GRIS BLANC NOIR)

cablage vers l'arduino : tous reliés au GND de l'arduino.

> Une nappe correspondant aux contacts du joystick.

Cablage vers l'arduino : 

pin :
-----------

8 : 	BLEU
9 :	ORANGE
10 :	VERT
11 :	JAUNE

----------------SHIELD DF ROBOTS DC MOTOR DRIVER 15A------------------------

pins arduino	pins shield
----------------------------
4 :		M2_EN
5 : 		M1_pwm
6 : 		M2_pwm
7 : 		M1_EN
5V:		5V	
GND:		GND

--------------------------------

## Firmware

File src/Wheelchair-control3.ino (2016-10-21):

/*
  /*
  # This Sample code is for testing the DC Motor Driver 2x15A_lite module. // Upgraded by @hugobiwan to drive an open source wheelchair for @myhumankit.

  # Editor : Phoebe
  # Date   : 2012.11.6
  # Ver    : 0.1
  # Product: DC Motor Driver 2x15A_lite
  # SKU    : DRI0018

  # Description:
  # Drive 2 motors with this DC Motor Driver module

  # Hardwares:
  1. Arduino UNO
  2. DC Motor Driver 2x15A_lite
  3. DC motors x2

  #Steps:
  1.Connect the M1_PWM & M2_PWM to UNO digital 5 & 6
  2.Connect the M1_EN & M2_EN to UNO digital 4 & 7
  3.Connect +5V & GND to UNO 5V & GND
  4.Connect joystick switches in this order on a clock beginning from noon : 9,10,11,12. Connect the Ground of the switches to the arduino Ground

  # Function for current sense and diagnosis,if you want to use
  please connect the IS pins to Arduino
  Connect LA_IS and RA_IS to UNO digital 2 at the same time
  Connect LB_IS and RB_IS to UNO digital 3 at the same time
*/
//declaration des broches de joystick;
int haut = 8;
int droite = 9;
int bas = 10;
int gauche = 11;

//declaration des etats de broches de joystick;

int etat_haut = 0;
int etat_droite = 0;
int etat_bas = 0;
int etat_gauche = 0;



int E1 = 5;     //M1 Speed Control
int E2 = 6;     //M2 Speed Control
int M1 = 4;     //M1 Direction Control
int M2 = 7;     //M1 Direction Control
int counter = 0;



void stop(void)                    //Stop
{
  digitalWrite(E1, 0);
  digitalWrite(M1, LOW);
  digitalWrite(E2, 0);
  digitalWrite(M2, LOW);
}

//Contrôle par joystick
//on cree un array des 4 contacts de joystick possibles
int joystick[4];
int y = 0; //sert à incrémenter des saut dans le tableau, dans la fonction loop
int val = 0; // ordre de mouvement - 8 mouvements possibles et le stop.


void advance(char a, char b)         //Move forward
{
  analogWrite (E1, a);     //PWM Speed Control
  digitalWrite(M1, HIGH);
  analogWrite (E2, b);
  digitalWrite(M2, HIGH);
}
void back_off (char a, char b)         //Move backward
{
  analogWrite (E1, a);
  digitalWrite(M1, LOW);
  analogWrite (E2, b);
  digitalWrite(M2, LOW);
}
void turn_L (char a, char b)            //Turn Left
{
  analogWrite (E1, a);
  digitalWrite(M1, LOW);
  analogWrite (E2, b);
  digitalWrite(M2, HIGH);
}
void turn_R (char a, char b)            //Turn Right
{
  analogWrite (E1, a);
  digitalWrite(M1, HIGH);
  analogWrite (E2, b);
  digitalWrite(M2, LOW);
}
void current_sense()                  // current sense and diagnosis
{
  int val1 = digitalRead(2);
  int val2 = digitalRead(3);
  if (val1 == HIGH || val2 == HIGH) {
    counter++;
    if (counter == 3) {
      counter = 0;
      Serial.println("Warning");
    }
  }
}

void setup(void)
{
  int i;
  for (i = 4; i <= 7; i++)
    pinMode(i, OUTPUT);
  Serial.begin(9600);      //Set Baud Rate
  Serial.println("Lancement du joystick");
  digitalWrite(E1, LOW);
  digitalWrite(E2, LOW);
  pinMode(2, INPUT);
  pinMode(3, INPUT);

  //ajout du joystick- broches numérotées dans le sens des aiguilles d'une montre avec la 10 en position midi

  pinMode(haut, INPUT); //
  pinMode(droite, INPUT);
  pinMode(bas, INPUT);
  pinMode(gauche, INPUT);

  //activation des internal pullups

  digitalWrite(haut, HIGH);
  digitalWrite(droite, HIGH);
  digitalWrite(bas, HIGH);
  digitalWrite(gauche, HIGH);
}

void loop(void)
{
  /*
    static unsigned long timePoint = 0;    // current sense and diagnosis,if you want to use this
    if(millis() - timePoint > 1000){       //function,please show it & don't forget to connect the IS pins to Arduino
    current_sense();
    timePoint = millis();
    }
  */


  //On défini le caractere cible par la position du joystick
  //par exemple on code sa position dans un tableau

  int joystick[] = {etat_haut, etat_droite, etat_bas, etat_gauche};

  //debug

  //lecture des broches

  etat_haut = digitalRead(haut);
  etat_droite = digitalRead(droite);
  etat_bas = digitalRead(bas);
  etat_gauche = digitalRead(gauche);

  //temoin
  Serial.println(etat_haut);
  Serial.println(etat_droite);
  Serial.println(etat_bas);
  Serial.println(etat_gauche);
  Serial.println("----------------------------------------------------");
  //delay(100);


  //Ensuite on va regarder les valeurs du tableau et affecter le caractère. 8 positions possibles + le stop

  //positions pour avancer

  if (etat_haut == 0 && etat_droite == 1 && etat_bas == 1 && etat_gauche == 1)
  {
    Serial.println("avance");
    //ordre de mouvement
    val = 1;
  }
  if (etat_haut == 0 && etat_droite == 0 && etat_bas == 1 && etat_gauche == 1)
  {
    Serial.println("avance droite");
    //ordre de mouvement
    val = 8;
  }
  if (etat_haut == 1 && etat_droite == 0 && etat_bas == 1 && etat_gauche == 1)
  {
    Serial.println("droite");
    val = 3;
    //ordre de mouvement
  }
  if (etat_haut == 1 && etat_droite == 0 && etat_bas == 0 && etat_gauche == 1)
  {
    Serial.println("recule droite");
    //ordre de mouvement
    val = 4;
  }
  if (etat_haut == 1 && etat_droite == 1 && etat_bas == 0 && etat_gauche == 1)
  {
    Serial.println("recule");
    //ordre de mouvement
    val = 5;
  }
  if (etat_haut == 1 && etat_droite == 1 && etat_bas == 0 && etat_gauche == 0)
  {
    Serial.println("recule gauche");
    //ordre de mouvement
    val = 6;
  }
  if (etat_haut == 1 && etat_droite == 1 && etat_bas == 1 && etat_gauche == 0)
  {
    Serial.println("gauche");
    //ordre de mouvement
    val = 7;
  }
  if (etat_haut == 0 && etat_droite == 1 && etat_bas == 1 && etat_gauche == 0)
  {
    Serial.println("avance gauche");
    //ordre de mouvement
    val = 2;
  }
  else if (etat_haut == 0 && etat_bas == 0 || etat_gauche == 0 && etat_droite == 0 || etat_haut == 1 && etat_droite == 1 && etat_bas == 1 && etat_gauche == 1) {
    Serial.println("stop");
    val = 9;
  }

  Serial.println("----------------------------------------------------");
  Serial.println(val);
  //delay(1000);
  Serial.println("----------------------------------------------------");
  //fin du serial
  //ON LANCE L'ORDRE DE MOUVEMENT
  bouge(val);
}





//on utilise la fonction deja codee mais on va ajouter des codes pour les diagonales

void bouge(int valeur) {


  switch (valeur)
  {
    case 1://Move Forward
      advance (255, 255);  //move forward in max speed
      break;
    //avance vers la avant droite (diagonale 1)
    case 2:
      advance (255, 120);  //move forward in max speed
      break;
    //avance vers arriere droite (diagonale 2)
    case 4:
      back_off (255, 120);
      break;
    //avance vers arriere gauche (diagonale 3)
    case 6:
      back_off (120, 255);
      break;
    //avance vers avant gauche (diagonale 4)
    case 8:
      advance (120, 255);
      break;
    case 5://Move Backward
      back_off (255, 255);  //move back in max speed
      break;
    case 7://Turn Left
      turn_L (100, 100);
      break;
    case 3://Turn Right
      turn_R (100, 100);
      break;
    case 9:
      stop();
      break;
    default :
      stop();
      break;
  }
}

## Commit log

2016-10-21 code arduino fonctionnel: correction du bug de direction inversée lors du recul par Hugobiwan
2016-10-21 debut de la fusion de la doc LibreOffice vers MarkDown
2016-10-21 ajout des media pour la doc
2016-10-21 schéma de connection par Hugo Biwan Kenobille
2016-10-24 slides de présentation du projet à l'issue du sprint au Fabrikarium avec insertion du lien vers depot github
2016-10-27 modèles 3d corrigés de Philippe Pacotte
    [boitier joistick.igs, boitier joistick.obj, boitier joistick.stl, boitier joistick.stp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]
2016-10-27 correction de la puissance envoyée aux moteurs. Par Hugobiwankinobi
2016-10-27 ajout de qq media
2016-11-07 première étape de l'assemblage sans les images
2016-11-07 gabarit de bout
2016-11-07 ajout media pour instructions de montage & gabarit
2016-11-07 assemblage du cadre avec photos
2016-11-07 more media pour instructions de montage & gabarit
2016-11-07 ajout media assemblage du cadre de base
2016-11-07 texte assemblage du cadre
2016-11-07 ajout media asssemblage des accoudoirs
2016-11-07 montage des roulettes half-life
2016-11-07 assemblage des roulettes well done this time
2016-11-08 media pour assemblage roues motrices
2016-11-08 plaque avec cercles à fixer sur le motoréducteur
2016-11-08 media pôur assemblage roues motoréducteurs
2016-11-08 media: detail assemblage montant arrière accoudoir
2016-11-10 essai avec bonne URL pour les 2 premières photos
2016-11-11 ajouts de légendes aux images actuelles
2016-12-13 photo avec la bonne rotation
2016-12-13 ajout plan SVG pour CNC de l'accoudoir
2016-12-13 images du chemin du cable 4 paires du joystick
2016-12-13 agrafage du passage de câble
2016-12-13 schéma de principe en mode photo quick and dirty
2016-12-13 squelette de l'assemblage du boîtier électrique
2016-12-13 ajout du schéma de cablage du driver tiré du wiki du fabricant DFRobot
2016-12-13 ### câblage des moteurs vers la carte driver
    petite manip pour caler les sens de rotation
2016-12-13 confection
    photos quick and dirty des crobards de Mme Veron
2016-12-13 ajout des photos des crobards pour la confection
2016-12-14 câblage du driver vers l'Arduino
2016-12-14 ménage dans les sources
